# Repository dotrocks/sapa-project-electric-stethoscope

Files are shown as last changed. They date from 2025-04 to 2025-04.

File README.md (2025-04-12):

# Electric Stethoscope

This project is a simple electric stethoscope that can be used to listen to the body sounds of a patient. Prepared for AGU SAPA capsule final project.

## Pre-requisites

### Hardware

- Arduino Uno
- 2 wire electret microphone
- Doctor's stethoscope
- Resistors
  - 1 x 1kΩ
  - 1 x 4.7kΩ
  - 2 x 10kΩ
  - 1 x 22kΩ
  - 1 x 100kΩ
- Capacitors
  - 2 x 10nF (Connected in series for 5nF)
  - 1 x 47nF
  - 1 x 1uF
- 1 x Low-Noise Operational Amplifier (NE5532, TL072, etc.)
- Breadboard
- Jumper wires
- Optional:
  - Soldering iron and its accessories
  - Pertinax board to solder the circuit (or you can simply buy a PCB)
  - 3D printer to print the box for the circuit

### Software

- Arduino IDE
- LTspice
- Python 3.6 or higher

## Running the project

- Clone the repository
- Connect Arduino Uno to your computer
- Build the circuit following the [circuit diagram](https://crcit.net/c/c403772aff41427b846746d022f3cfba)
- Connect circuit to Arduino Uno
- Open the Arduino IDE and upload the `arduino/arduino.ino` file to the Arduino Uno
- Run Python server by running the following commands:

  ```bash
  cd app
  pip install -r requirements.txt
  python main.py
  ```

- Enjoy!

## Circuit Diagram

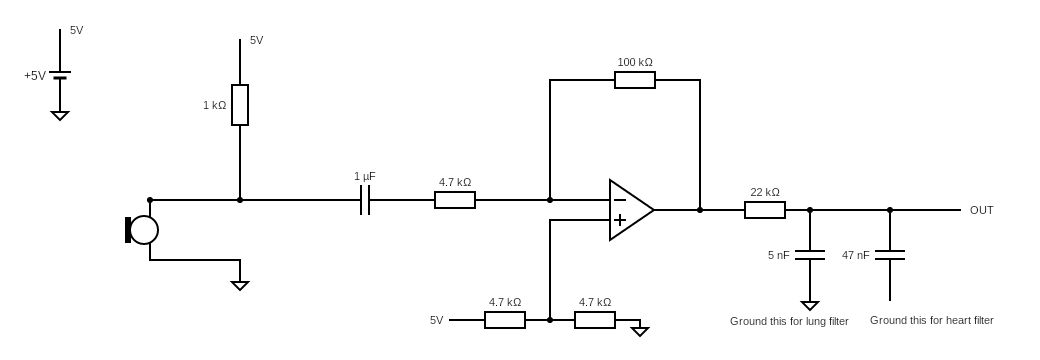
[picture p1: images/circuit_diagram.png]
Circuit Diagram


## Gallery

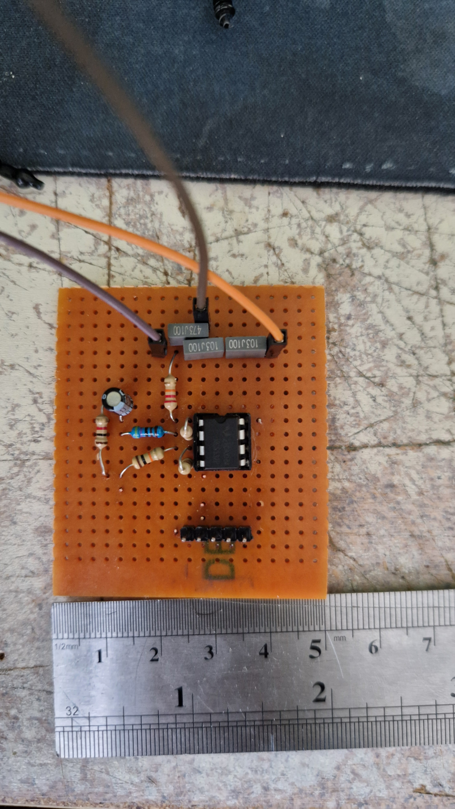
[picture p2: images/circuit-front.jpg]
Circuit Front

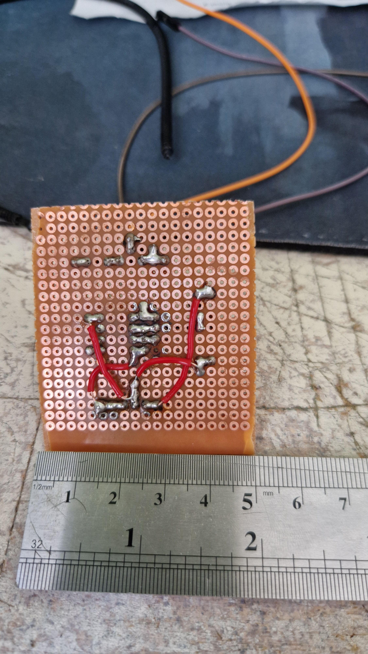
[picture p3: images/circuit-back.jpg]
Circuit Back

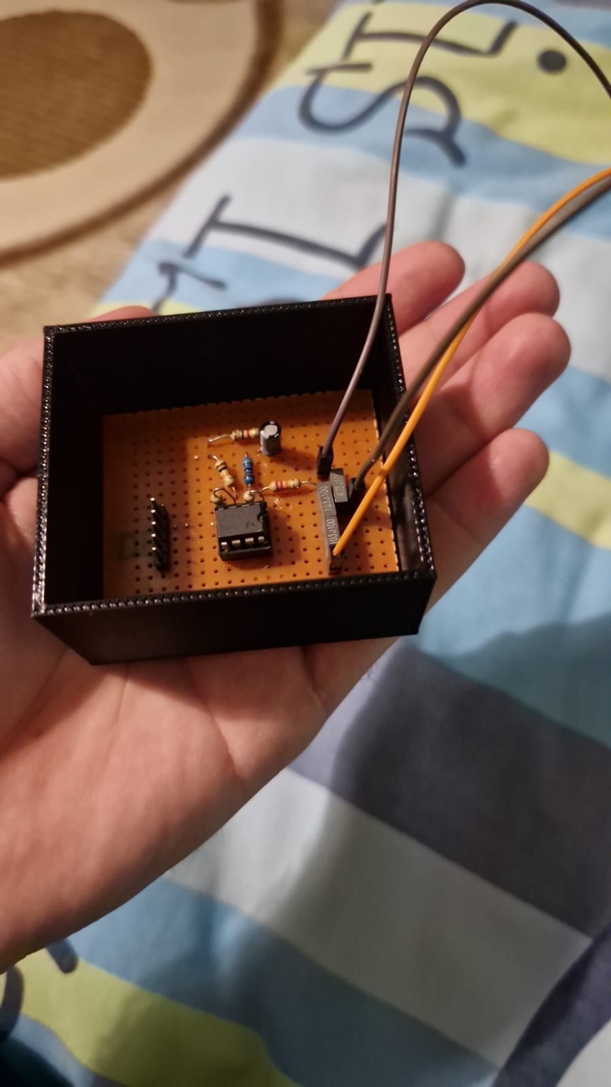
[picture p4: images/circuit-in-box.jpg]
Circuit in Box

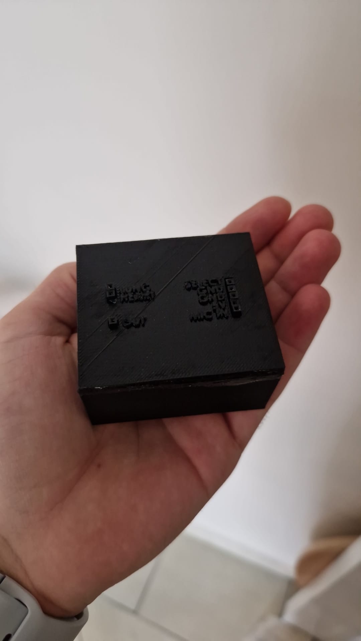
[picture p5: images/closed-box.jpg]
Closed Box


## Project Team

- Barış DEMİRCİ - <agu@338.rocks>
- Selin Nisa AKGÖL - <selinnisa.akgol@agu.edu.tr>
- Nuri İNCEÖZ - <nuri.inceoz@agu.edu.tr>

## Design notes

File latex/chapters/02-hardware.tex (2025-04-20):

\chapter{Hardware Development}

\section{Circuit Design \& Simulation}

\subsection{Electret Microphone Circuit}
First, tried to simulate the electrec microphone circuit using LTSpice. The circuit is shown in the figure below.

\begin{figure}[h]
	\centering
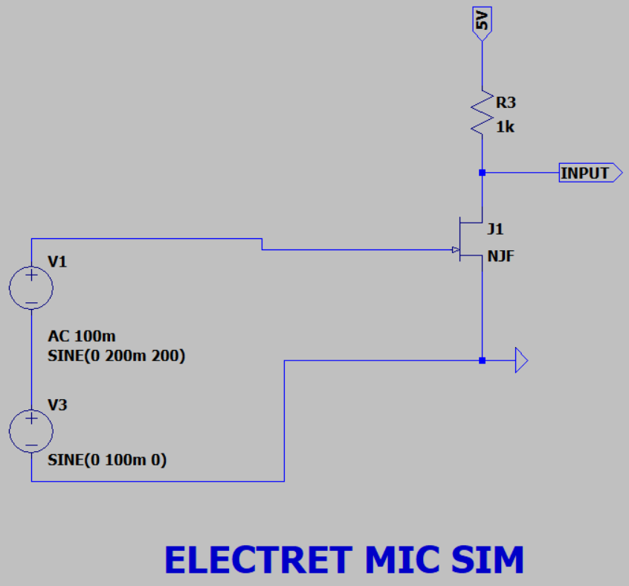
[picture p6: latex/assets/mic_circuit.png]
	
	\caption{Electret Microphone Circuit}
	\label{fig:mic_circuit}
\end{figure}

A 2-wire electrec microphone consists of one capacitor and one N-channel JFET. Using the circuit shown in Figure \ref{fig:mic_circuit}, we we able to acquire the voice signal from the microphone. Signal was too weak and too noisy to be used directly, so we needed to amplify and filter it.

\newpage
\thispagestyle{plain}

\subsection{Filter Circuit}

\subsubsection{High-Pass \& DC Filter}
Incoming signal was oscillating around 5V and had a lot of noise. We were planning to Arduino Uno for signal processing, so we needed to convert the signal to 0-5V range. We also needed to filter the noise. We designed a filter circuit using LTSpice.
\begin{figure}[h]
	\centering
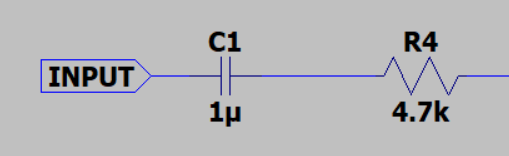
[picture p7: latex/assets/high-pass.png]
	
	\caption{High-Pass Filter Circuit}
	\label{fig:hp_filter_circuit}
\end{figure}

Used a passive high-pass filter setup as shown in Figure \ref{fig:hp_filter_circuit} for both filtering DC offset and low frequency noise. The cutoff frequency can be calculated using the formula:
\begin{equation}\label{eq:filter_cutoff}
	f_c = \frac{1}{2\pi RC}
\end{equation}
In our case, we used R = $4.7k\Omega$ and C = $1\mu$F, so the cutoff frequency was $33.8$Hz. This filter was able to filter out the DC offset and low frequency noise.

\subsubsection{Low-Pass Filter}

\begin{figure}[h]
	\centering
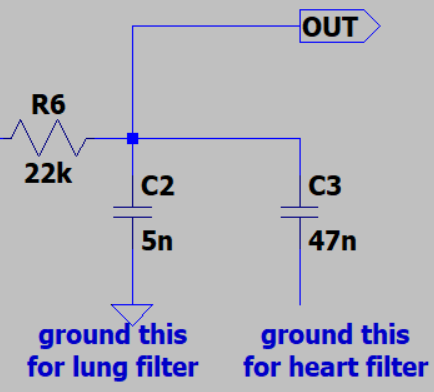
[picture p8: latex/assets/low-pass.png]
	
	\caption{Low-Pass Filter Circuit}
	\label{fig:lp_filter_circuit}
\end{figure}

Again, used a passive low-pass filter setup as shown in Figure \ref{fig:lp_filter_circuit} for filtering high frequency noise. The cutoff frequency can be calculated using the formula \ref{eq:filter_cutoff}. In our case, we used R = $22k\Omega$ and C = $5$nF for lung, C = $47$nF for heart, so the cutoff frequency was $153$Hz for heart and $1446$Hz for lung. This filter was able to filter out the high frequency noise.

\newpage
\thispagestyle{plain}

\subsection{Amplifier Circuit}

\begin{figure}[h]
	\centering
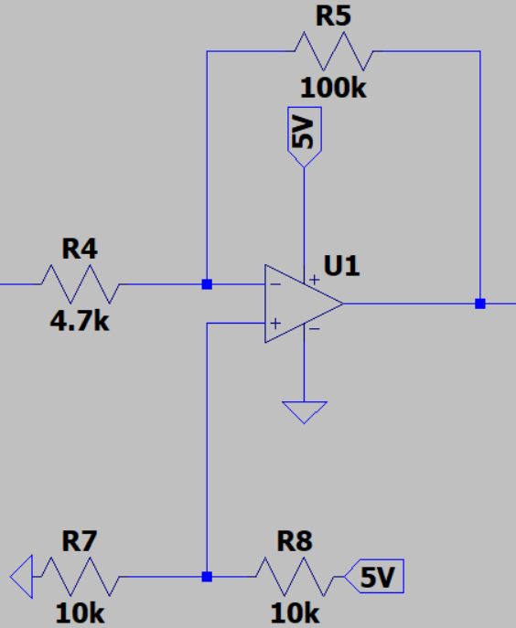
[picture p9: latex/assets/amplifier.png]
	
	\caption{Amplifier Circuit}
	\label{fig:amplifier_circuit}
\end{figure}

We used an inverting op-amp circuit for amplifying the signal, adding 2.5V DC bias, and inverting the signal to its original state (because the signal was inverted by the electrec mic). The gain of the amplifier can be calculated using the formula:

\begin{equation}\label{eq:amplifier_gain}
	G = -\frac{R_f}{R_1}
\end{equation}

In our case, we used $R_1 = 4.7k\Omega$ and $R_f = 100k\Omega$, so the gain was approximately $-20$. This amplifier was able to amplify the signal to a usable level. For DC bias, we used a voltage divider ciruit to get 2.5V and connected it to the non-inverting input of the op-amp, which made our signal oscillate around 2.5V.

\newpage
\thispagestyle{plain}

\subsection{Final Circuit}

After connecting everything together, the final circuit looked like this:

\begin{figure}[h]
	\centering
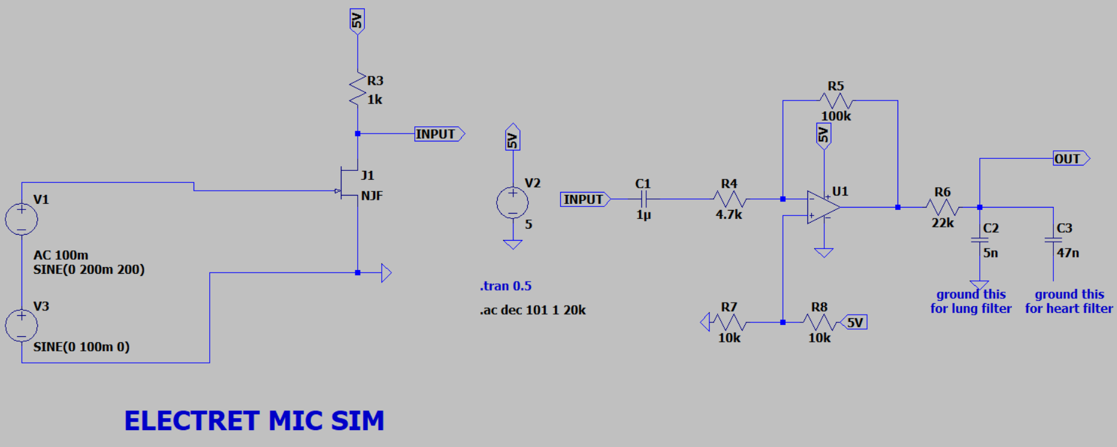
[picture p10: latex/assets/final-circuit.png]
	
	\caption{Final Circuit}
	\label{fig:final_circuit}
\end{figure}

To test the circuit, we used a function generator to simulate the electrec microphone signal. We were able to get the signal from the microphone, amplify it, and filter it successfully. After building the circuit we ran an AC simulation on LTSpice and checked the cutoff frequencies.

\begin{table}[h]
	\begin{tabular}{l|l|l|}
		\cline{2-3}
		                                                & \textbf{Analytical Cutoff Frequency} & \textbf{Simulation Result} \\ \hline
		\multicolumn{1}{|l|}{\textbf{High-Pass}}        & 33.8Hz                               & 26.7Hz                     \\ \hline
		\multicolumn{1}{|l|}{\textbf{Low-Pass (Heart)}} & 153Hz                                & 205Hz                      \\ \hline
		\multicolumn{1}{|l|}{\textbf{Low-Pass (Lung)}}  & 1466Hz                               & 1530Hz                     \\ \hline
	\end{tabular}
	\caption{Cutoff Frequencies}
	\label{tab:cutoff_frequencies}
\end{table}

According to \textcite{Debbal2020}, these frequencies are suitable for heartbeat detection and according to \textcite{Gross2000}, these frequencies are suitable for lung sound detection.

\newpage
\thispagestyle{plain}

\section{Prototype Design}

\subsection{Breadboard Prototype}
We have built the circuit in Figure \ref{fig:final_circuit} on a breadboard and measured output voltages using an oscilloscope.

\begin{figure}[h]
	\centering
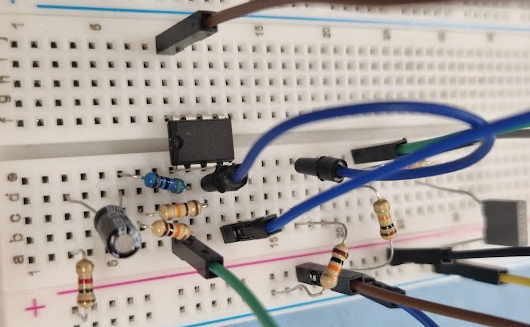
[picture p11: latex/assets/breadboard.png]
	
	\caption{Breadboard Prototype}
	\label{fig:breadboard_prototype}
\end{figure}

\begin{figure}[h]
	\centering
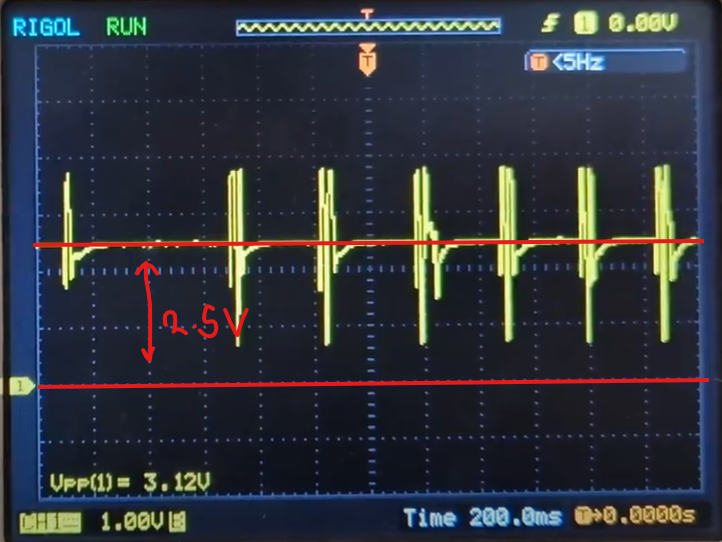
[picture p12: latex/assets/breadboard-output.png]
	
	\caption{Breadboard Prototype Output}
	\label{fig:breadboard_prototype_output}
\end{figure}

Output was exactly as expected. We were able to get the signal from the microphone, amplify it, give 2.5V DC bias, and filter it successfully.

\newpage
\thispagestyle{plain}

\subsection{Pertinax Board Design}

After making sure that the circuit works as expected, we soldered the circuit parts to perforated pertinax board as shown in Figure \ref{fig:pertinax_board_design}.

\begin{figure}[h]
	\centering
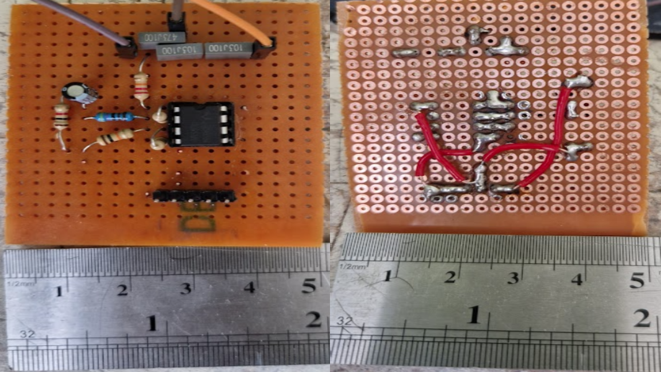
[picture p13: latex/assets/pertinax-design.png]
	
	\caption{Pertinax Board Design}
	\label{fig:pertinax_board_design}
\end{figure}

\newpage
\thispagestyle{plain}

\subsection{Casing Design}

We designed a casing for the prototype using SolidWorks. Casing has required pin headers for microphone, Arduino, and power supply connections.

\begin{figure}[h]
	\centering
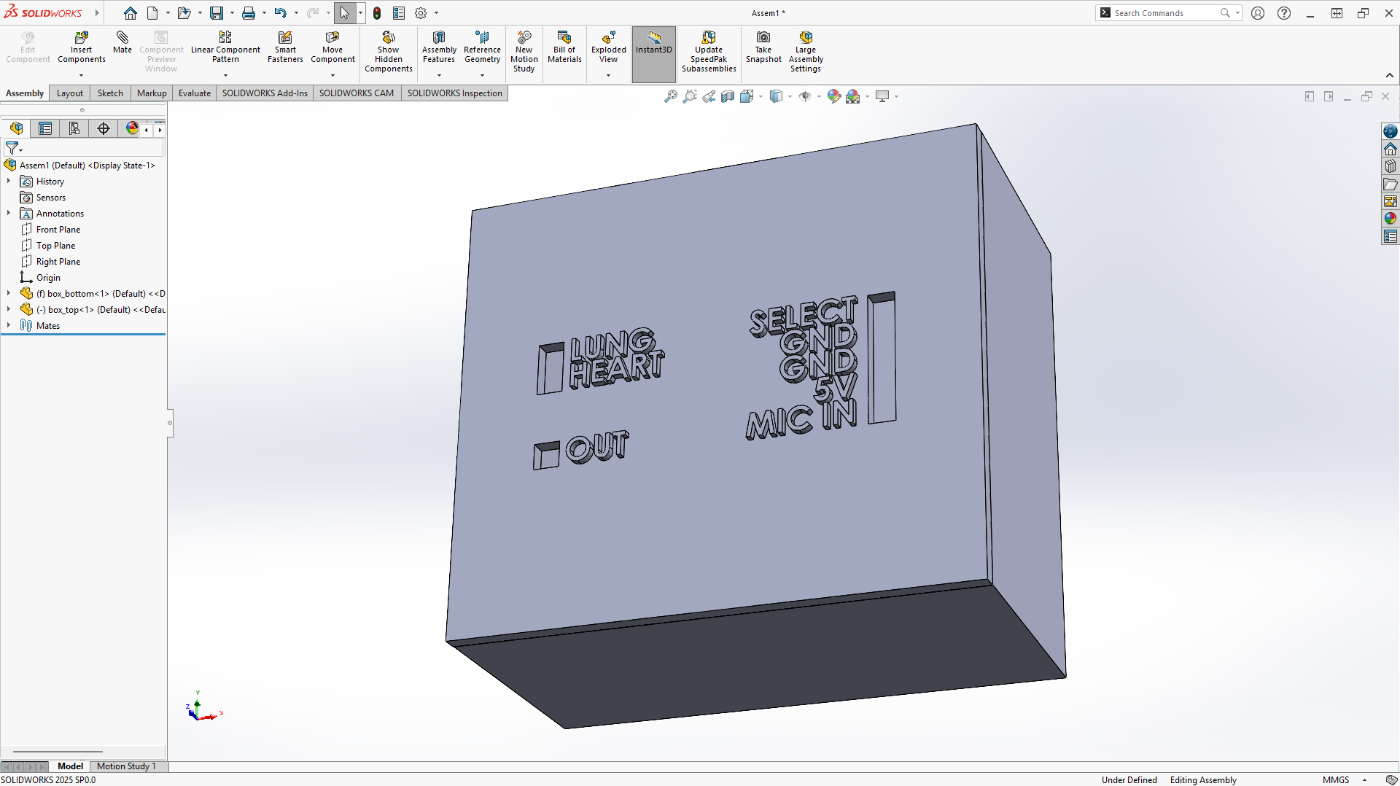
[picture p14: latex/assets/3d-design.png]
	
	\caption{Casing Design}
	\label{fig:casing_design}
\end{figure}

\begin{figure}[h]
	\centering
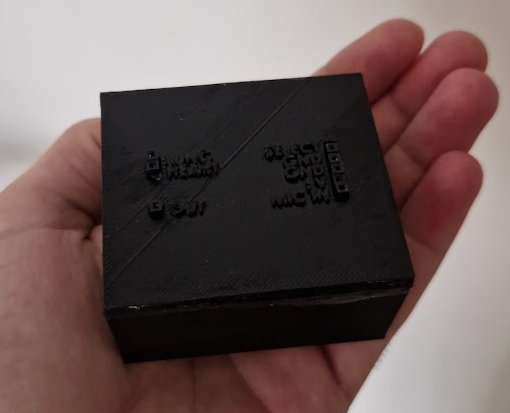
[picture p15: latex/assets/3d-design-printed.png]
	
	\caption{Casing Design Printed}
	\label{fig:casing_design_printed}
\end{figure}

Our first prototype is worked as expected so we decided to use it as our final prototype. By putting the prototype in the casing, we completed the hardware development phase.

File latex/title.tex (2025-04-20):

\begin{center}
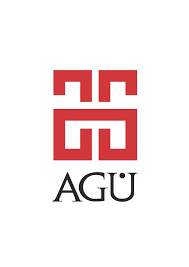
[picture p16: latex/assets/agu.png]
	

	\Huge
	\textbf{Abdullah Gül University}

	\vspace{0.3cm}
	Department of Electrical and Electronics Engineering

	\vspace{1cm}
	\Huge
	\textbf{\paperTitle}

	\vspace{0.3cm}
	\Huge
	\paperSubTitle{}

	\vspace{0.8cm}
	\large
	\vspace{0.5cm}
	\LARGE
	\vspace{1.5cm}
	\textbf{}
	\vfill
	\vspace{0.8cm}
	\Large
\end{center}

\begin{tabbing}
	\hspace*{1em}\= \hspace*{9em} \= \kill
	\> \textbf{Project Team:} \>  \\
	\> Barış DEMİRCİ \> agu@338.rocks \\
	\> Selin Nisa AKGÖL \> selinnisa.akgol@agu.edu.tr \\
	\> Nuri İNCEÖZ \> nuri.inceoz@agu.edu.tr \\
	\>  \\
	\> December 30, 2024 \\
\end{tabbing}

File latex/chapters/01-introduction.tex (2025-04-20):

\chapter{Introduction}

\section{Background}
The stethoscope, a critical tool in medical diagnostics for nearly two centuries, has been a staple in physicians’ practices worldwide. With technological advancements, digital stethoscopes have emerged as modern alternatives, offering enhanced auscultation capabilities. These devices are cost-effective easy to use and capable of capturing both normal and abnormal breath sounds with high accuracy. This project aims to develop an electronic stethoscope system capable of acquiring and processing acoustic signals from various human body parts.

\section{Objective}
The primary goal is to design an electronic stethoscope system that acquires acoustic body sounds, converts them into digital signals, and transmits them to a computer for real-time monitoring and analysis. The system will include hardware and software components for:

\begin{itemize}
	\item Signal acquisition
	\item Amplification and filtering
	\item Digital conversion and transmission
	\item Real-time tracking via a graphical user interface (GUI)
\end{itemize}

\section{Scope}

\begin{itemize}
	\item The project involves designing custom amplification and filtering circuits without using commercial modules.
	\item Arduino will handle digital conversion and data transmission.
	\item Python will be used for GUI development, ensuring smooth signal monitoring and analysis.
\end{itemize}

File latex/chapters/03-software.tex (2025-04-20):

\chapter{Software Development}

\section{Arduino Code}\label{sec:arduino_code}

We used an Arduino Uno for signal transmission. It already has its own 10-bit 0-5V ADC for analog signal transmission. We already made the necessary signal processing on the hardware side, our signal oscillates around 2.5V and has a range of 0-5V. We can start to read the signal using Arduino without any problem or any signal loss.

Before starting to measure the analog signal, we measured the reading speed using the following benchmark code in order to decide what sampling rate we should use:

\begin{lstlisting}[language=C++, caption=Analog Read Benchmark Code, label=lst:analog_read_benchmark]
void loop() {
    unsigned long start = micros();
    analogRead(A0);
    unsigned long end = micros();
    Serial.println(end - start);
}
\end{lstlisting}

The code reads the analog signal from pin A0 and prints the time taken to read the signal in microseconds. We used this code to measure the analog signal reading speed of the Arduino Uno. The average time taken to read the analog signal was 112$\mu$s. This means that the Arduino Uno can read the analog signal at a rate of 8.9kHz. This is more than enough for our project, as the maximum frequency of the signal we are trying to measure is 2kHz.

According to \textcite{Wikiedia-NyquistShannon2024}, Nyquist-Shannon Sampling Theorem says the minimum sampling rate should be twice the maximum frequency of the signal. So, we need a minimum sampling rate of 4kHz, but more is better.

\newpage
\thispagestyle{plain}

Arduino Uno can read the analog signal at a rate of 8.9kHz, which is more than enough for our project but for stability (because read speed vary around 108$\mu$s to 116$\mu$s according to our benchmarks), we decided to use a sampling rate of 8kHz (125$\mu$s, more than benchmark average). To achieve this, we used the following code:

\begin{lstlisting}[language=C++, caption=Arduino Code for 8kHz Sampling Rate, label=lst:arduino_code]
void loop() {
    unsigned long startedAt = micros();

    // Send the sensor value to the serial port
    int sensorValue = analogRead(analogPin);
    Serial.println(sensorValue);

    unsigned long endedAt = micros();
    unsigned long timeTook = endedAt - startedAt;

    // 125us = 8kHz sampling rate
    unsigned long timeRemaining = 125 - timeTook;

    // Wait for the remaining time
    // this approach will give us 8kHz sampling rate in theory
    // But in practice, it may not be exactly 8kHz 
    // but it is good enough for our purposes
    if (timeRemaining > 0) {
        delayMicroseconds(timeRemaining);
    }
}
\end{lstlisting}

This code reads the analog signal from pin A0, prints the signal value to the serial port, and waits for the remaining time to achieve an 8kHz sampling rate. This code will give us an 8kHz sampling rate in theory, but in practice, it may not be exactly 8kHz. However, it is good enough for our purposes.

\newpage
\thispagestyle{plain}

While this code prints the analog signal value to the serial port at 8kHz sampling rate, we used a Python script to read the serial port. Sometimes, Python cannot read the serial data correctly because this process is an asynchronous process. Maybe Arduino sends half of the data before Python is ready to read it. To prevent this, we can use starting and ending characters for the serial communication and keep a buffer in Python. We used the following code for this purpose:

\begin{lstlisting}[language=C++, caption=Arduino Code with Start and End Characters, label=lst:arduino_code_start_end]
const int analogPin = A0;

// Define the starting and ending characters 
// for the serial communication. 
// Sometimes python cannot read the serial data incorrectly. 
// To prevent this, we can use starting and ending characters.
const String startingChar = "S";
const String endingCar = "E";

void loop() {
    unsigned long startedAt = micros();

    int sensorValue = analogRead(analogPin);
    
    // Print the value with starting and ending characters
    Serial.print(startingChar);
    Serial.print(sensorValue);
    Serial.println(endingCar);

    // On serial port: 
    // SxxxxE -> S: Start, E: End, xxxx: Sensor Value
    // Example
    // S338E -> S: Start, E: End, 338: Sensor Value

    unsigned long endedAt = micros();
    unsigned long timeTook = endedAt - startedAt;

    // 125us = 8kHz sampling rate
    unsigned long timeRemaining = 125 - timeTook;

    // Wait for the remaining time
    // this approach will give us 8kHz sampling rate in theory
    // But in practice, it may not be exactly 8kHz 
    // but it is good enough for our purposes
    if (timeRemaining > 0) {
        delayMicroseconds(timeRemaining);
    }
}
\end{lstlisting}

This code prints the analog signal value to the serial port with starting and ending characters. This way, we can prevent Python from reading the serial data incorrectly.

\newpage
\thispagestyle{plain}

\section{Python Code}

We used Python to read the serial port, process the analog signal and show the real-time signal on a GUI. As we mentioned in Section \ref{sec:arduino_code}, Arduino Code, we used starting and ending characters for the serial communication. We used these characters to prevent Python from reading the serial data incorrectly. We used the following code to read the serial port:

\begin{lstlisting}[language=Python, caption=Python Code to Read Serial Port, label=lst:python_code_read_serial]
# Read data from serial port. Read Arduino code for more details
data_buffer = ""
while ser.in_waiting > 0:
    try:
        char = ser.read().decode("utf-8")
        data_buffer += char

        if "E" in data_buffer and "S" in data_buffer:
            try:
                start_index = data_buffer.index("S")
                end_index = data_buffer.index("E")
                value_str = data_buffer[start_index + 1 : end_index]
                if value_str.isdigit():
                    analog_value = int(value_str)

                    # Normalize and zero center because 
                    # most of the dsp functions 
                    # require zero centered data
                    normalized = (
                        (analog_value / 1024.0) * 5.0
                    ) - 2.5

                    # Append the normalized value to the list
                    # So that we can plot it later
                    analog_data.append(normalized)
                    time_data.append(time.time())

                    while time_data and (time_data[-1] - time_data[0] > 5):
                        time_data.popleft()
                        analog_data.popleft()
            except ValueError:
                pass
            data_buffer = ""

    except UnicodeDecodeError:
        data_buffer = ""
    except Exception:
        data_buffer = ""
\end{lstlisting}

\newpage
\thispagestyle{plain}

With this code, we read the serial port and process the analog signal. We normalized the analog signal to be zero-centered because most of the digital signal processing functions require zero-centered data. We also kept the last 5 seconds of the data in the list to plot it later.

While these codes are the most important parts of the software development, we also developed a GUI to show the real-time signal which we are not mentioning the code here. The GUI is developed using the tkinter and matplotlib library. You can always check the full code from the GitHub repository of the project, which is given in Appendix \ref{sec:appendix_a}.

\begin{figure}[h]
	\centering
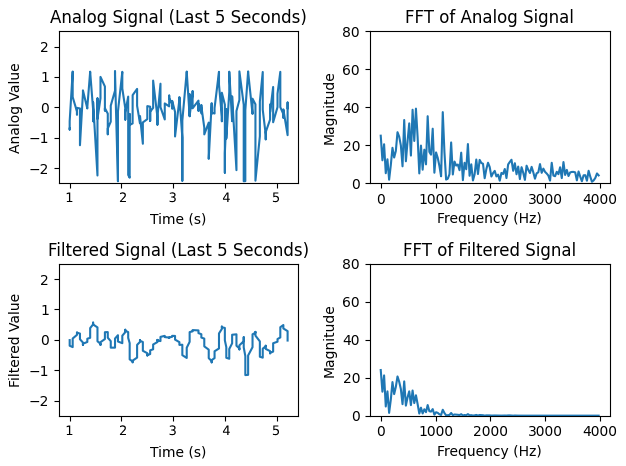
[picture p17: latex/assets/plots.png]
	
	\caption{GUI of the Project}
	\label{fig:gui}
\end{figure}

\begin{figure}[h]
	\centering
	\begin{minipage}{0.5\textwidth}
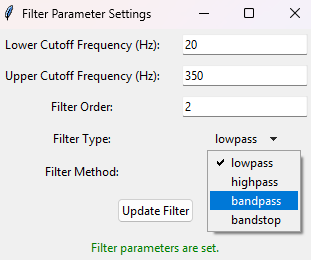
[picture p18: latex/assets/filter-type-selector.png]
		
		\caption{Filter Type Selector}
		\label{fig:gui-filter-type-selector}
	\end{minipage}%
	\begin{minipage}{0.5\textwidth}
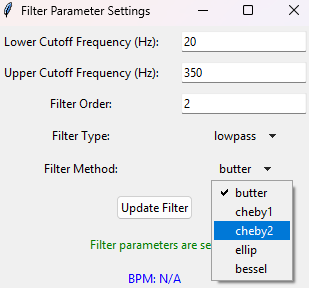
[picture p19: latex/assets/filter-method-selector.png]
		
		\caption{Filter Method Selector}
		\label{fig:gui-filter-method-selector}
	\end{minipage}
\end{figure}

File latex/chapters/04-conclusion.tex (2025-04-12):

\chapter{Conclusion}

The development of the electronic stethoscope demonstrates the integration of electronics, software, and medical knowledge to create a modern diagnostic tool. With its ability to capture, process, and analyze body sounds, this device provides a valuable addition to healthcare diagnostics. Further improvements in signal processing and hardware miniaturization could make this tool indispensable for clinicians.

This project demonstrated how easy to design a digital stethoscope using off-the-shelf components. The device was able to capture and process body sounds, and the results were displayed on a computer screen. With further development, the device could be used for real-time diagnosis and monitoring of patients.

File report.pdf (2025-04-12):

SAPA Capsule Project | Electric Stethoscope | December 30, 2024

# Abdullah G¨ul University

# Department of Electrical and Electronics Engineering

# SAPA Capsule Project

# Electric Stethoscope

Project Team:
Barı¸s DEM˙IRC˙I agu@338.rocks
Selin Nisa AKGOL selinnisa.akgol@agu.edu.tr ¨
Nuri ˙INCEOZ | nuri.inceoz@agu.edu.tr ¨

December 30, 2024

# Contents

1 Introduction | 3
1.1 Background | | 3
1.2 Objective | | 3
1.3 Scope | | 3
2 Hardware Development | 4
2.1 Circuit Design & Simulation | | 4
2.1.1 | Electret Microphone Circuit | | 4
2.1.2 | Filter Circuit | | 5
2.1.3 | Amplifier Circuit | | 6
2.1.4 | Final Circuit | | 7
2.2 Prototype Design | | 8
2.2.1 | Breadboard Prototype | | 8
2.2.2 | Pertinax Board Design | | 9
2.2.3 | Casing Design | | 10
3 Software Development | 11
3.1 Arduino Code | | 11
3.2 Python Code | | 14
4 Conclusion | | 16
Appendix | | 17
Github Repository | | 17
Bibliography | | 18

# Chapter 1

# Introduction

## 1.1 Background

The stethoscope, a critical tool in medical diagnostics for nearly two centuries, has been a staple in physicians’ practices worldwide. With technological advancements, digital stethoscopes have emerged as modern alternatives, offering enhanced auscultation capabilities. These devices are cost-effective easy to use and capable of capturing both normal and abnormal breath sounds with high accuracy. This project aims to develop an electronic stethoscope system capable of acquiring and processing acoustic signals from various human body parts.

## 1.2 Objective

The primary goal is to design an electronic stethoscope system that acquires acoustic body sounds, converts them into digital signals, and transmits them to a computer for real-time monitoring and analysis. The system will include hardware and software components for:

Signal acquisition

Amplification and filtering

Digital conversion and transmission

Real-time tracking via a graphical user interface (GUI)

## 1.3 Scope

The project involves designing custom amplification and filtering circuits without using commercial modules.

Arduino will handle digital conversion and data transmission.

Python will be used for GUI development, ensuring smooth signal monitoring and analysis.

# Chapter 2

# Hardware Development

## 2.1 Circuit Design & Simulation

### 2.1.1 Electret Microphone Circuit

First, tried to simulate the electrec microphone circuit using LTSpice. The circuit is shown in the figure below.

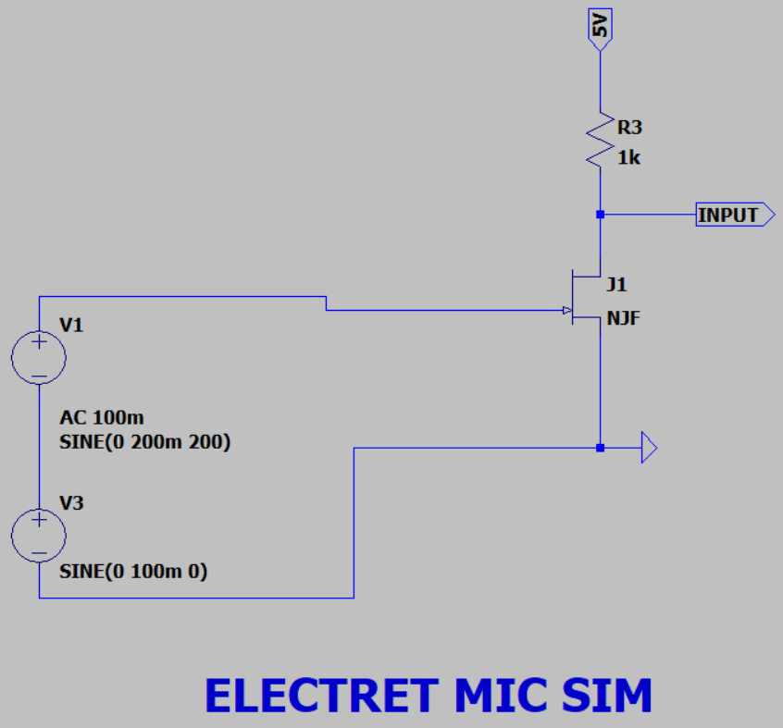
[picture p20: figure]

Figure 2.1: Electret Microphone Circuit

A 2-wire electrec microphone consists of one capacitor and one N-channel JFET. Using the circuit shown in Figure 2.1, we we able to acquire the voice signal from the microphone. Signal was too weak and too noisy to be used directly, so we needed to amplify and filter it.

### 2.1.2 Filter Circuit

High-Pass & DC Filter

Incoming signal was oscillating around 5V and had a lot of noise. We were planning to Arduino Uno for signal processing, so we needed to convert the signal to 0-5V range. We also needed to filter the noise. We designed a filter circuit using LTSpice.

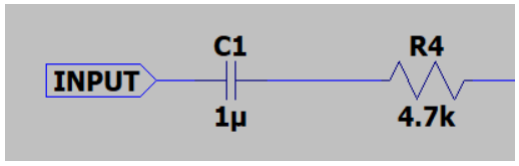
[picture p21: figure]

Figure 2.2: High-Pass Filter Circuit

Used a passive high-pass filter setup as shown in Figure 2.2 for both filtering DC offset and low frequency noise. The cutoff frequency can be calculated using the formula:

fc =

1
2πRC | (2.1)

In our case, we used R = 4.7kΩ and C = 1µF, so the cutoff frequency was 33.8Hz. This filter was able to filter out the DC offset and low frequency noise.

Low-Pass Filter


Figure 2.3: Low-Pass Filter Circuit

Again, used a passive low-pass filter setup as shown in Figure 2.3 for filtering high frequency noise. The cutoff frequency can be calculated using the formula 2.1. In our case, we used R = 22kΩ and C = 5nF for lung, C = 47nF for heart, so the cutoff frequency was 153Hz for heart and 1446Hz for lung. This filter was able to filter out the high frequency noise.

### 2.1.3 Amplifier Circuit

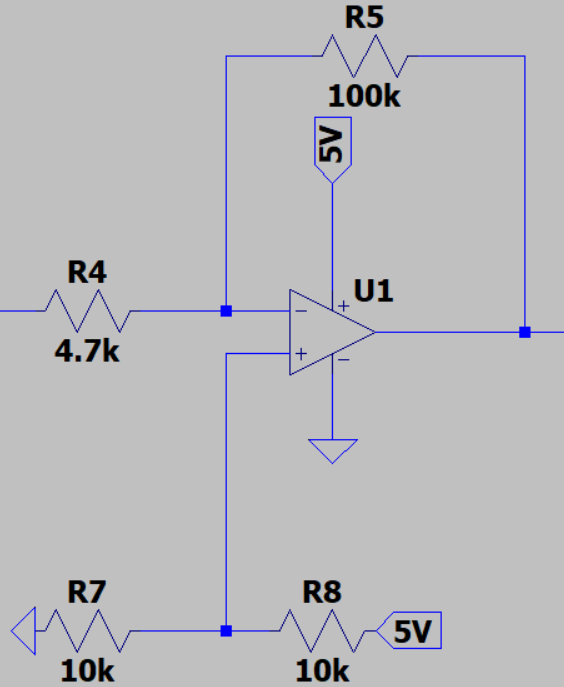
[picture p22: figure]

Figure 2.4: Amplifier Circuit

We used an inverting op-amp circuit for amplifying the signal, adding 2.5V DC bias, and inverting the signal to its original state (because the signal was inverted by the electrec mic). The gain of the amplifier can be calculated using the formula:

G = −

Rf
R1

(2.2)

In our case, we used R1 = 4.7kΩ and Rf = 100kΩ, so the gain was approximately −20. This amplifier was able to amplify the signal to a usable level. For DC bias, we used a voltage divider ciruit to get 2.5V and connected it to the non-inverting input of the op-amp, which made our signal oscillate around 2.5V.

### 2.1.4 Final Circuit

After connecting everything together, the final circuit looked like this:

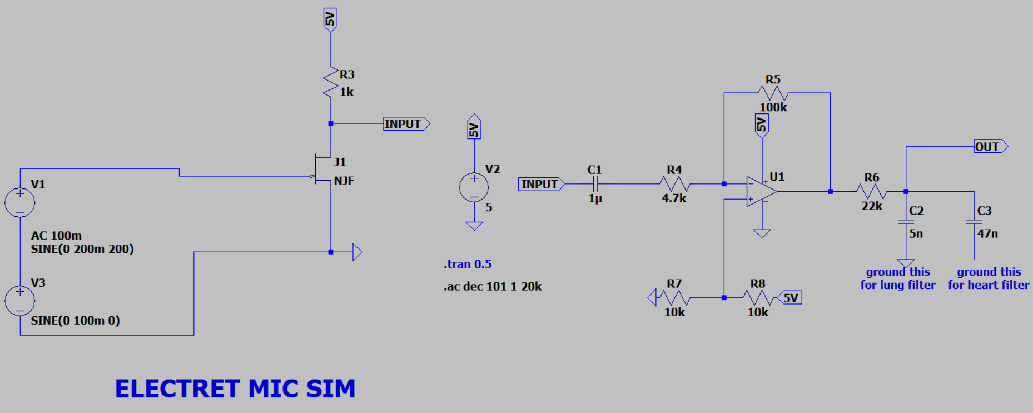
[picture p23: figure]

Figure 2.5: Final Circuit

To test the circuit, we used a function generator to simulate the electrec microphone signal. We were able to get the signal from the microphone, amplify it, and filter it successfully. After building the circuit we ran an AC simulation on LTSpice and checked the cutoff frequencies.

Analytical Cutoff Frequency | Simulation Result
High-Pass | 33.8Hz | 26.7Hz
Low-Pass (Heart) | 153Hz | 205Hz
Low-Pass (Lung) | 1466Hz | 1530Hz

Table 2.1: Cutoff Frequencies

According to Debbal (2020), these frequencies are suitable for heartbeat detection and according to Gross et al. (2000), these frequencies are suitable for lung sound detection.

## 2.2 Prototype Design

### 2.2.1 Breadboard Prototype

We have built the circuit in Figure 2.5 on a breadboard and measured output voltages using an oscilloscope.

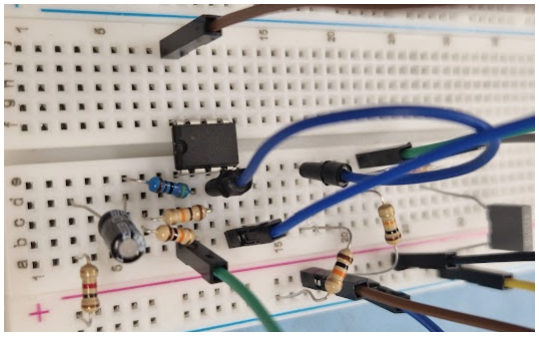
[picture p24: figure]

Figure 2.6: Breadboard Prototype

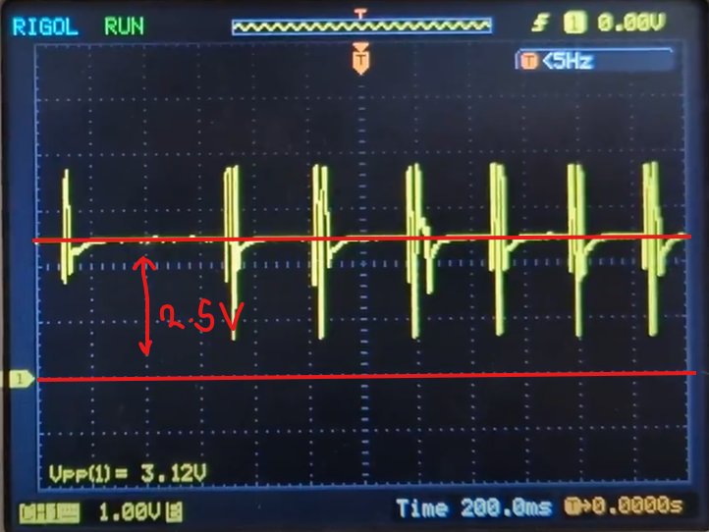
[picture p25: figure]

Figure 2.7: Breadboard Prototype Output

Output was exactly as expected. We were able to get the signal from the microphone, amplify it, give 2.5V DC bias, and filter it successfully.

### 2.2.2 Pertinax Board Design

After making sure that the circuit works as expected, we soldered the circuit parts to perforated pertinax board as shown in Figure 2.8.

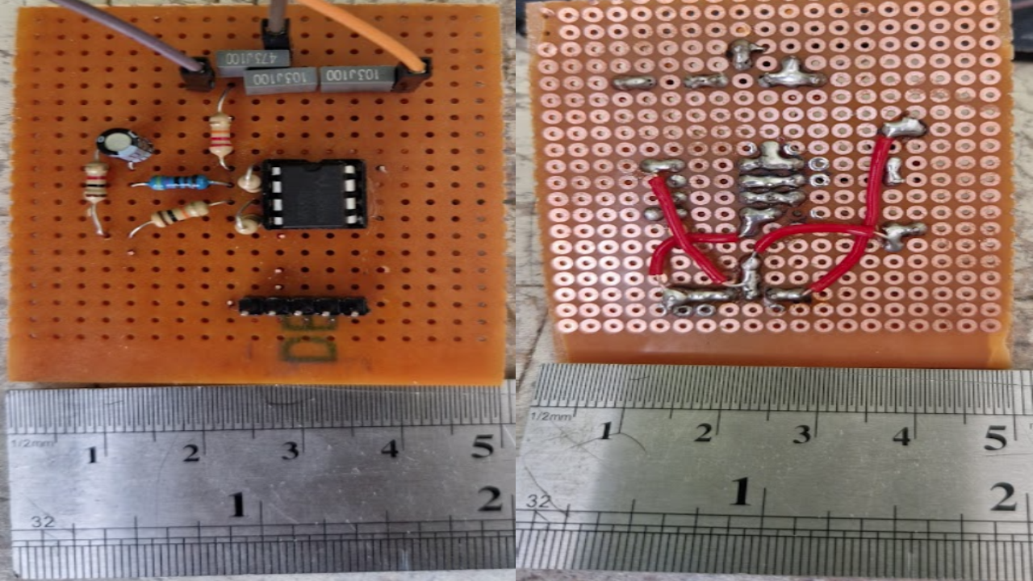
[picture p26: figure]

Figure 2.8: Pertinax Board Design

### 2.2.3 Casing Design

We designed a casing for the prototype using SolidWorks. Casing has required pin headers for microphone, Arduino, and power supply connections.

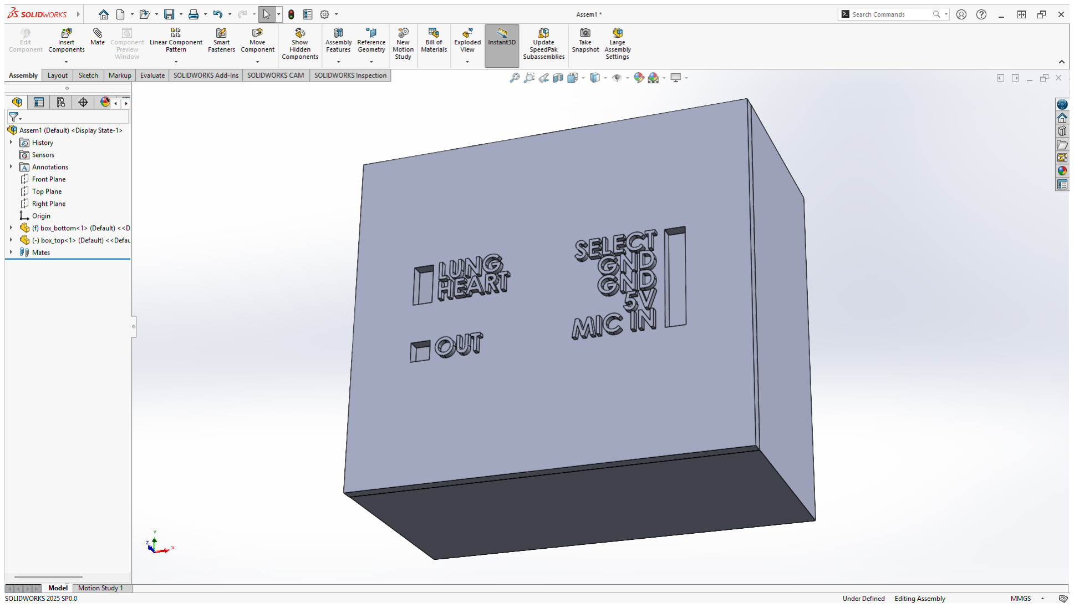
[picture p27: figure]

Figure 2.9: Casing Design


Figure 2.10: Casing Design Printed

Our first prototype is worked as expected so we decided to use it as our final prototype. By putting the prototype in the casing, we completed the hardware development phase.

# Chapter 3

# Software Development

## 3.1 Arduino Code

We used an Arduino Uno for signal transmission. It already has its own 10-bit 0-5V ADC for analog signal transmission. We already made the necessary signal processing on the hardware side, our signal oscillates around 2.5V and has a range of 0-5V. We can start to read the signal using Arduino without any problem or any signal loss.
Before starting to measure the analog signal, we measured the reading speed using the following benchmark code in order to decide what sampling rate we should use:

Listing 3.1: Analog Read Benchmark Code void loo p ( ) {
unsigned long s t a r t = mic ro s ( ) ; analogRead (A0 ) ;
unsigned long end = mic ro s ( ) ;
S e r i a l . p r i n t l n ( end = s t a r t ) ;
}

The code reads the analog signal from pin A0 and prints the time taken to read the signal in microseconds. We used this code to measure the analog signal reading speed of the Arduino Uno. The average time taken to read the analog signal was 112µs. This means that the Arduino Uno can read the analog signal at a rate of 8.9kHz. This is more than enough for our project, as the maximum frequency of the signal we are trying to measure is 2kHz.
According to Wikipedia (2024), Nyquist-Shannon Sampling Theorem says the minimum sampling rate should be twice the maximum frequency of the signal. So, we need a minimum sampling rate of 4kHz, but more is better.

Arduino Uno can read the analog signal at a rate of 8.9kHz, which is more than enough for our project but for stability (because read speed vary around 108µs to 116µs according to our benchmarks), we decided to use a sampling rate of 8kHz (125µs, more than benchmark average). To achieve this, we used the following code:

Listing 3.2: Arduino Code for 8kHz Sampling Rate void loo p ( ) {
unsigned long s ta r t e dA t = mic ro s ( ) ;

// Send t h e s e n s o r v a l u e t o t h e s e r i a l p o r t int s e n so rVal u e = analogRead ( analogPin ) ;
S e r i a l . p r i n t l n ( s e n so rVal u e ) ;

unsigned long endedAt = mic ro s ( ) ;
unsigned long timeTook = endedAt = s ta r t e dA t ;

// 125 us = 8kHz s am pl ing r a t e
unsigned long timeRemaining = 125 = timeTook ;

// Wait f o r t h e rema in ing t ime
// t h i s approach w i l l g i v e us 8kHz s am pl ing r a t e in t h e o r y // But in p r a c t i c e , i t may no t be e x a c t l y 8kHz
// b u t i t i s good enough f o r our p u r p o s e s
i f ( timeRemaining > 0 ) {
d ela yMi c ro s e co n d s ( timeRemaining ) ;
}
}

This code reads the analog signal from pin A0, prints the signal value to the serial port, and waits for the remaining time to achieve an 8kHz sampling rate. This code will give us an 8kHz sampling rate in theory, but in practice, it may not be exactly 8kHz. However, it is good enough for our purposes.

While this code prints the analog signal value to the serial port at 8kHz sampling rate, we used a Python script to read the serial port. Sometimes, Python cannot read the serial data correctly because this process is an asynchronous process. Maybe Arduino sends half of the data before Python is ready to read it. To prevent this, we can use starting and ending characters for the serial communication and keep a buffer in Python. We used the following code for this purpose:

Listing 3.3: Arduino Code with Start and End Characters const int analogPin = A0 ;

// De f ine t h e s t a r t i n g and en d ing c h a r a c t e r s
// f o r t h e s e r i a l commun icat ion .
// Sometimes py thon canno t read t h e s e r i a l d a t a i n c o r r e c t l y . // To p r e v e n t t h i s , we can use s t a r t i n g and en d ing c h a r a c t e r s . const S t ri n g s t a r ti n g C h a r = ”S” ;
const S t ri n g endingCar = ”E” ;

void loo p ( ) {
unsigned long s ta r t e dA t = mic ro s ( ) ;

int s e n so rVal u e = analogRead ( analogPin ) ;

// P r i n t t h e v a l u e w i t h s t a r t i n g and en d ing c h a r a c t e r s S e r i a l . p r i n t ( s t a r ti n g C h a r ) ;
S e r i a l . p r i n t ( s e n so rVal u e ) ;
S e r i a l . p r i n t l n ( endingCar ) ;

// On s e r i a l p o r t :
// SxxxxE => S : S t a r t , E : End , xxxx : Sensor Value // Example
// S338E => S : S t a r t , E : End , 3 3 8 : Sensor Value

unsigned long endedAt = mic ro s ( ) ;
unsigned long timeTook = endedAt = s ta r t e dA t ;

// 125 us = 8kHz s am pl ing r a t e
unsigned long timeRemaining = 125 = timeTook ;

// Wait f o r t h e rema in ing t ime
// t h i s approach w i l l g i v e us 8kHz s am pl ing r a t e in t h e o r y // But in p r a c t i c e , i t may no t be e x a c t l y 8kHz
// b u t i t i s good enough f o r our p u r p o s e s
i f ( timeRemaining > 0 ) {
d ela yMi c ro s e co n d s ( timeRemaining ) ;
}
}

This code prints the analog signal value to the serial port with starting and ending characters. This way, we can prevent Python from reading the serial data incorrectly.

## 3.2 Python Code

We used Python to read the serial port, process the analog signal and show the real-time signal on a GUI. As we mentioned in Section 3.1, Arduino Code, we used starting and ending characters for the serial communication. We used these characters to prevent Python from reading the serial data incorrectly. We used the following code to read the serial port:

Listing 3.4: Python Code to Read Serial Port # Read d a t a from s e r i a l p o r t . Read Ardu ino code f o r more d e t a i l s d a t a b uff e r = ””
while s e r . i n w a i t i n g > 0 :
try :
cha r = s e r . read ( ) . decode ( ” u tf =8” )
d a t a b uff e r += cha r

i f ”E” in d a t a b uff e r and ”S” in d a t a b uff e r : try :
s t a r t i n d e x = d a t a b uff e r . inde x ( ”S” )
e n d i n d e x = d a t a b uff e r . inde x ( ”E” )
v a l u e s t r = d a t a b uff e r [ s t a r t i n d e x + 1 : e n d i n d e x ] i f v a l u e s t r . i s d i g i t ( ) :
a n al o g v al u e = int ( v a l u e s t r )

# Normal ize and z e r o c e n t e r bec a u se # most o f t h e dsp f u n c t i o n s

# r e q u i r e z e r o c e n t e r e d d a t a

no rmaliz e d = (
( a n al o g v al u e / 1 0 2 4. 0 ) * | 5. 0
) = | 2. 5

# Append t h e n o rm al i ze d v a l u e t o t h e l i s t # So t h a t we can p l o t i t l a t e r

a nalog da ta . append ( no rmali z ed )
tim e da ta . append ( time . time ( ) )

while tim e da ta and ( tim e da ta [ =1] = tim e da ta [ 0 ] > 5 ) : tim e da ta . p o p l ef t ( )
a nalog da ta . p o p l ef t ( )
except ValueE r ro r :
pass
d a t a b uff e r = ””

except UnicodeDecodeError : d a t a b uff e r = ””
except Excep tion :
d a t a b uff e r = ””

With this code, we read the serial port and process the analog signal. We normalized the analog signal to be zero-centered because most of the digital signal processing functions require zero-centered data. We also kept the last 5 seconds of the data in the list to plot it later.
While these codes are the most important parts of the software development, we also developed a GUI to show the real-time signal which we are not mentioning the code here. The GUI is developed using the tkinter and matplotlib library. You can always check the full code from the GitHub repository of the project, which is given in Appendix 4.


Figure 3.1: GUI of the Project

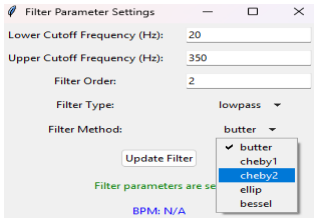
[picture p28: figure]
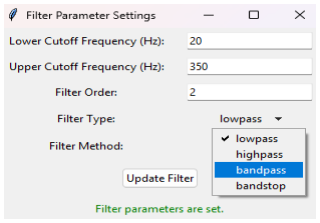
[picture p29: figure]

Figure 3.2: Filter Type Selector | Figure 3.3: Filter Method Selector

# Chapter 4

# Conclusion

The development of the electronic stethoscope demonstrates the integration of electronics, software, and medical knowledge to create a modern diagnostic tool. With its ability to capture, process, and analyze body sounds, this device provides a valuable addition to healthcare diagnostics. Further improvements in signal processing and hardware miniaturization could make this tool indispensable for clinicians.
This project demonstrated how easy to design a digital stethoscope using off-the-shelf components. The device was able to capture and process body sounds, and the results were displayed on a computer screen. With further development, the device could be used for real-time diagnosis and monitoring of patients.

# Appendix

## Appendix A: Github Repositoy

https://github.com/dotrocks/sapa-project-electric-stethoscope

# Bibliography

Debbal, S. M. E. A. (2020). Analysis of the four heart sounds statistical study and spectro-temporal characteristics. Clinical Case Reports Journal, 1 (4), 1–13. https: // clinicalcasereportsjournal. com/article/1000046/analysis - of - the - four - heart -sounds-statistical-study-and-spectro-temporal-characteristics (https://clinicalcasereportsjournal.com/article/1000046/analysis-of-the-four-heart-sounds-statistical-study-and-spectro-temporal-characteristics)
Gross, V., Dittmar, A., Penzel, T., Sch¨uttler, F., & von Wichert, P. (2000). The relationship between normal lung sounds, age, and gender. American Journal of Respiratory and Critical Care Medicine, 162 (3), 905–909. https://doi.org/10.1164/ajrccm.162.3.9905104 (https://doi.org/10.1164/ajrccm.162.3.9905104)
Wikipedia. (2024). Nyquist-Shannon sampling theorem — Wikipedia, the free encyclopedia [Online; accessed 29-December-2024].

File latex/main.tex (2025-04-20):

\def\paperTitle{SAPA Capsule Project}
\def\paperSubTitle{Electric Stethoscope}

\documentclass[
	12pt,twoside,a4paper
]{report}

\usepackage{graphicx}
\usepackage[margin=1in]{geometry}
\usepackage{fancyhdr}
\usepackage[utf8]{inputenc}
\usepackage{etoc}
\usepackage{xcolor, soul}
\usepackage{listings}
\usepackage{amsmath}
\usepackage{lipsum}
\usepackage{pgfplots}
\usepackage{hyperref}
\usepackage{tikz}
\usepackage{circuitikz}
\usepackage[style=apa, backend=biber]{biblatex}

\addbibresource{refs.bib}
\DeclareLanguageMapping{english}{english-apa}

\sethlcolor{yellow}

\fancypagestyle{plain}{
	\fancyhf{}
	\fancyhead[l]{\paperTitle}
	\fancyhead[c]{\paperSubTitle}
	\fancyhead[r]{December 30, 2024}
	\fancyfoot[le, ro]{Page \thepage}
	\setlength{\headheight}{15pt}
	\renewcommand{\headrulewidth}{0.2pt}
	\renewcommand{\footrulewidth}{0.2pt}
}	

\thispagestyle{plain}

\renewcommand{\etocaftertitlehook}{\thispagestyle{plain}}
\renewcommand{\etocaftertochook}{\thispagestyle{plain}}

\begin{document}
\include{title}
\tableofcontents

\include{chapters/01-introduction}
\include{chapters/02-hardware}
\include{chapters/03-software}
\include{chapters/04-conclusion}

\newpage
\thispagestyle{plain}

\chapter*{Appendix}
\addcontentsline{toc}{chapter}{Appendix}

\section*{Appendix A: Github Repositoy}\label{sec:appendix_a}
\addcontentsline{toc}{section}{Github Repository}
\url{https://github.com/dotrocks/sapa-project-electric-stethoscope}

\printbibliography{}
\addcontentsline{toc}{chapter}{Bibliography}
\end{document}

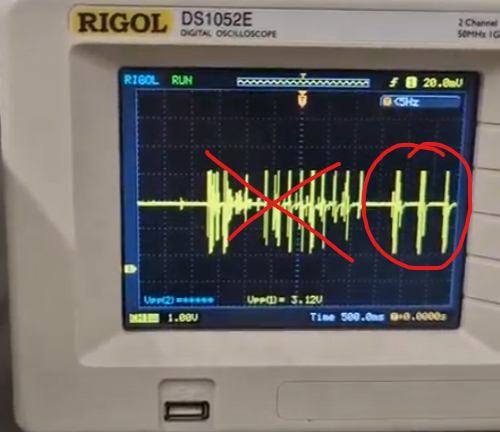
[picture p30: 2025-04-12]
latex/assets/oscilloscope-heartbeat.png

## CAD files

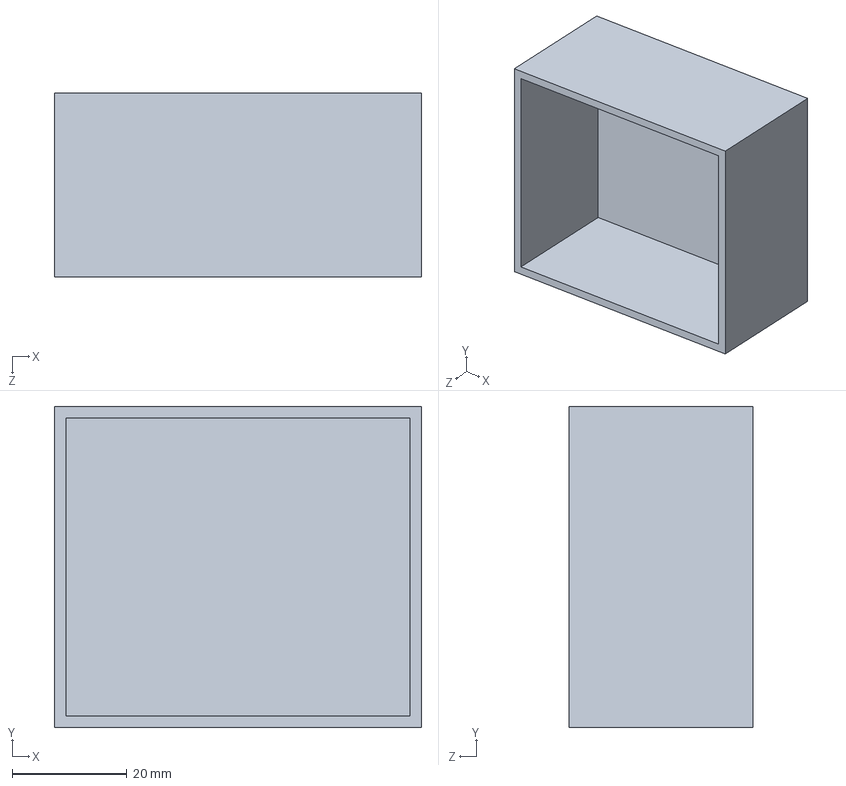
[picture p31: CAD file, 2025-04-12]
3d/box_bottom.SLDPRT
64.0 x 56.0 x 32.0 mm

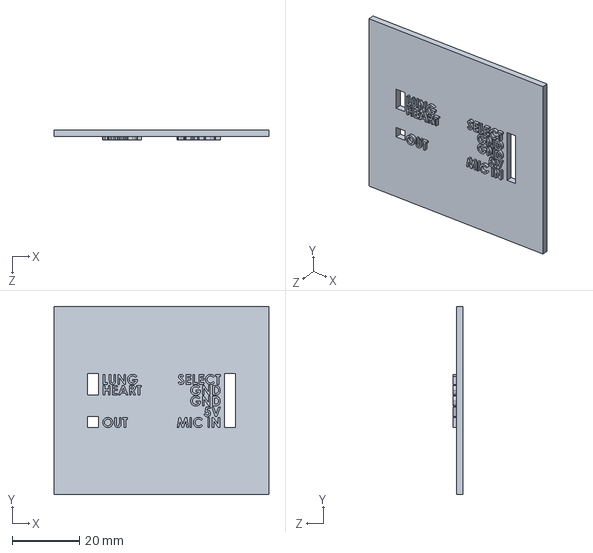
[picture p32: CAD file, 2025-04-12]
3d/box_top.SLDPRT
64.0 x 56.0 x 3.00 mm

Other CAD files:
3d/box_bottom.STL
3d/box_top.STL

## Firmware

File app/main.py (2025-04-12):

import serial
import time
import numpy as np
import matplotlib.pyplot as plt
import matplotlib.animation as animation
from collections import deque
from scipy import signal
import tkinter as tk
from tkinter import ttk
import threading
from scipy.signal import find_peaks

# Serial Configuration
arduino_port = "COM3"  # Replace with your Arduino port
baud_rate = 9600
sample_rate = 8000  # Samples per second
buffer_size = sample_rate * 5  # 5 seconds of data

# Initial Filter parameters
lower_cutoff_freq = 20  # Lower cutoff frequency in Hz
upper_cutoff_freq = 350  # Upper cutoff frequency in Hz
filter_order = 2  # Filter order
filter_type = "lowpass"  # Initial filter type
filter_method = "butter"  # Initial filter method

# Connect to Arduino
try:
    ser = serial.Serial(arduino_port, baud_rate)
    time.sleep(2)  # Wait for Arduino to initialize
    print(f"Connected to Arduino on {arduino_port}")
except serial.SerialException as e:
    print(f"Error connecting to Arduino: {e}")
    exit()

# Data Buffers
analog_data = deque(maxlen=buffer_size)
filtered_data = deque(maxlen=buffer_size)
time_data = deque(maxlen=buffer_size)

# Initialize filter
nyquist_freq = 0.5 * sample_rate


def create_filter():
    # Select cutoff frequencies based on filter type
    if filter_type == "lowpass":
        normalized_cutoff = upper_cutoff_freq / nyquist_freq
    elif filter_type == "highpass":
        normalized_cutoff = lower_cutoff_freq / nyquist_freq
    else:
        normalized_cutoff = [
            lower_cutoff_freq / nyquist_freq,
            upper_cutoff_freq / nyquist_freq,
        ]

    # Create filter based on method
    if filter_method == "butter":
        return signal.butter(
            filter_order, normalized_cutoff, btype=filter_type, analog=False
        )

    elif filter_method == "cheby1":
        return signal.cheby1(
            filter_order, 0.5, normalized_cutoff, btype=filter_type, analog=False
        )

    elif filter_method == "cheby2":
        return signal.cheby2(
            filter_order, 40, normalized_cutoff, btype=filter_type, analog=False
        )

    elif filter_method == "ellip":
        return signal.ellip(
            filter_order, 0.5, 40, normalized_cutoff, btype=filter_type, analog=False
        )

    elif filter_method == "bessel":
        return signal.bessel(
            filter_order, normalized_cutoff, btype=filter_type, analog=False
        )


# Initialize filter coefficients
b, a = create_filter()

# Initialize plot
fig, ((ax1, ax2), (ax3, ax4)) = plt.subplots(2, 2)
(line1,) = ax1.plot([], [])
(line2,) = ax2.plot([], [])
(line3,) = ax3.plot([], [])
(line4,) = ax4.plot([], [])

ax1.set_title("Analog Signal (Last 5 Seconds)")
ax1.set_xlabel("Time (s)")
ax1.set_ylabel("Analog Value")
ax1.set_ylim(-2.5, 2.5)

ax2.set_title("FFT of Analog Signal")
ax2.set_xlabel("Frequency (Hz)")
ax2.set_ylabel("Magnitude")
ax2.set_ylim(0, 80)

ax3.set_title("Filtered Signal (Last 5 Seconds)")
ax3.set_xlabel("Time (s)")
ax3.set_ylabel("Filtered Value")
ax3.set_ylim(-2.5, 2.5)

ax4.set_title("FFT of Filtered Signal")
ax4.set_xlabel("Frequency (Hz)")
ax4.set_ylabel("Magnitude")
ax4.set_ylim(0, 80)

fig.tight_layout()


# Function to animate the plot
def animate(i):
    # Read data from serial port. Read Arduino code for more details
    data_buffer = ""
    while ser.in_waiting > 0:
        try:
            char = ser.read().decode("utf-8")
            data_buffer += char

            if "E" in data_buffer and "S" in data_buffer:
                try:
                    start_index = data_buffer.index("S")
                    end_index = data_buffer.index("E")
                    value_str = data_buffer[start_index + 1 : end_index]
                    if value_str.isdigit():
                        analog_value = int(value_str)
                        normalized = (
                            (analog_value / 1024.0) * 5.0
                        ) - 2.5  # Normalize and zero center because most of the dsp functions require zero centered data

                        analog_data.append(normalized)
                        time_data.append(time.time())

                        while time_data and (time_data[-1] - time_data[0] > 5):
                            time_data.popleft()
                            analog_data.popleft()
                except ValueError:
                    pass
                data_buffer = ""

        except UnicodeDecodeError:
            data_buffer = ""
        except Exception:
            data_buffer = ""

    if len(analog_data) > 1:
        relative_times = np.array(list(time_data)) - time_data[0]

        # Apply filter
        filtered = signal.lfilter(b, a, list(analog_data))
        filtered_data.extend(filtered)
        while len(filtered_data) > len(analog_data):
            filtered_data.popleft()

        line1.set_data(relative_times, list(analog_data))
        ax1.relim()
        ax1.autoscale_view()

        # FFT of analog signal
        yf = np.fft.fft(list(analog_data))
        T = 1.0 / sample_rate
        xf = np.fft.fftfreq(len(analog_data), T)[: len(analog_data) // 2]
        line2.set_data(xf, np.abs(yf[0 : len(analog_data) // 2]))
        ax2.relim()
        ax2.autoscale_view()

        line3.set_data(relative_times, list(filtered_data))
        ax3.relim()
        ax3.autoscale_view()

        # FFT of filtered signal
        yff = np.fft.fft(list(filtered_data))
        xff = np.fft.fftfreq(len(filtered_data), T)[: len(filtered_data) // 2]
        line4.set_data(xff, np.abs(yff[0 : len(filtered_data) // 2]))
        ax4.relim()
        ax4.autoscale_view()

    return (line1, line2, line3, line4)


# Function to calculate BPM, not working properly :D
def calculate_bpm():
    if len(filtered_data) > 1:
        # Detect peaks in the filtered signal (which corresponds to heartbeats)
        peaks, _ = find_peaks(
            list(filtered_data), height=0.5, distance=10  # sample_rate // 2
        )  # Adjust height and distance if needed

        if len(peaks) > 1:  # Ensure there are at least two peaks
            # Calculate the time intervals between successive peaks
            peak_times = np.array([time_data[i] for i in peaks])
            peak_intervals = np.diff(
                peak_times
            )  # Time intervals between successive peaks

            avg_interval = np.mean(peak_intervals)  # Average interval in seconds
            bpm = 60 / avg_interval  # BPM calculation (beats per minute)

            bpm_label.config(text=f"BPM: {bpm:.2f}")  # Display BPM in the GUI
        else:
            bpm_label.config(text="BPM: Not enough data")  # Not enough peaks detected
    else:
        bpm_label.config(text="BPM: Not enough data")  # Not enough filter


# Function to update filter parameters
def update_filter_params():
    global b, a, lower_cutoff_freq, upper_cutoff_freq, filter_order, filter_type, filter_method

    try:
        new_lower_cutoff = float(lower_cutoff_entry.get())
        new_upper_cutoff = float(upper_cutoff_entry.get())
        new_order = int(order_entry.get())
        new_filter_type = filter_type_var.get()
        new_filter_method = filter_method_var.get()

        # Validate filter parameters according to Nyquist sapmling theorem
        if new_lower_cutoff <= 0 or new_order <= 0:
            raise ValueError("Cutoff frequencies and order must be positive.")
        if new_lower_cutoff >= nyquist_freq or (
            new_filter_type in ["bandpass", "bandstop"]
            and new_upper_cutoff >= nyquist_freq
        ):
            raise ValueError("Cutoff frequencies must be less than Nyquist frequency.")
        if (
            new_filter_type in ["bandpass", "bandstop"]
            and new_lower_cutoff >= new_upper_cutoff
        ):
            raise ValueError(
                "For bandpass/bandstop, lower cutoff must be less than upper cutoff."
            )

        lower_cutoff_freq = new_lower_cutoff
        upper_cutoff_freq = new_upper_cutoff
        filter_order = new_order
        filter_type = new_filter_type
        filter_method = new_filter_method

        # Update filter coefficients
        b, a = create_filter()

        status_label.config(
            text=f"Filter updated: Method={filter_method}, Type={filter_type}, Cutoff={lower_cutoff_freq}-{upper_cutoff_freq}Hz, Order={filter_order}",
            foreground="green",
        )
    except ValueError as ve:
        status_label.config(text=f"Error: {ve}", foreground="red")


# Tkinter GUI setup
def create_gui():
    global lower_cutoff_entry, upper_cutoff_entry, order_entry, status_label, filter_type_var, filter_method_var, bpm_label

    root = tk.Tk()
    root.title("Filter Parameter Settings")

    # Lower Cutoff Frequency
    ttk.Label(root, text="Lower Cutoff Frequency (Hz):").grid(
        row=0, column=0, padx=10, pady=5
    )
    lower_cutoff_entry = ttk.Entry(root)
    lower_cutoff_entry.grid(row=0, column=1, padx=10, pady=5)
    lower_cutoff_entry.insert(0, str(lower_cutoff_freq))

    # Upper Cutoff Frequency
    ttk.Label(root, text="Upper Cutoff Frequency (Hz):").grid(
        row=1, column=0, padx=10, pady=5
    )
    upper_cutoff_entry = ttk.Entry(root)
    upper_cutoff_entry.grid(row=1, column=1, padx=10, pady=5)
    upper_cutoff_entry.insert(0, str(upper_cutoff_freq))

    # Filter Order
    ttk.Label(root, text="Filter Order:").grid(row=2, column=0, padx=10, pady=5)
    order_entry = ttk.Entry(root)
    order_entry.grid(row=2, column=1, padx=10, pady=5)
    order_entry.insert(0, str(filter_order))

    # Filter Type
    ttk.Label(root, text="Filter Type:").grid(row=3, column=0, padx=10, pady=5)
    filter_type_var = tk.StringVar(value=filter_type)
    filter_type_menu = ttk.OptionMenu(
        root,
        filter_type_var,
        filter_type,
        "lowpass",
        "highpass",
        "bandpass",
        "bandstop",
    )
    filter_type_menu.grid(row=3, column=1, padx=10, pady=5)

    # Filter Method
    ttk.Label(root, text="Filter Method:").grid(row=4, column=0, padx=10, pady=5)
    filter_method_var = tk.StringVar(value=filter_method)
    filter_method_menu = ttk.OptionMenu(
        root,
        filter_method_var,
        filter_method,
        "butter",
        "cheby1",
        "cheby2",
        "ellip",
        "bessel",
    )
    filter_method_menu.grid(row=4, column=1, padx=10, pady=5)

    # BPM Label
    bpm_label = ttk.Label(
        root, text="BPM: N/A", foreground="blue"
    )  # Define bpm_label here
    bpm_label.grid(row=7, column=0, columnspan=2, pady=10)

    # Update Button
    update_button = ttk.Button(root, text="Update Filter", command=update_filter_params)
    update_button.grid(row=5, column=0, columnspan=2, pady=10)

    # Calculate BPM Button
    calculate_bpm_button = ttk.Button(root, text="Calculate BPM", command=calculate_bpm)
    calculate_bpm_button.grid(row=8, column=0, columnspan=2, pady=10)

    # Status Label
    status_label = ttk.Label(
        root, text="Filter parameters are set.", foreground="green"
    )
    status_label.grid(row=6, column=0, columnspan=2, pady=5)

    root.mainloop()


# Start Tkinter GUI in a separate thread
threading.Thread(target=create_gui, daemon=True).start()

# Start the animation
ani = animation.FuncAnimation(
    fig,
    animate,
    interval=1 / 144,  # 144 Hz refresh rate, adjust as needed
    blit=True,
    cache_frame_data=False,
)
plt.show()
